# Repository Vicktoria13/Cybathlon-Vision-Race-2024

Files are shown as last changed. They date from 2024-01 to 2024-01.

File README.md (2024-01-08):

# Projet Cybathlon 2024: prise en main des ressources

Le Cybathlon-VIS est une compétition scientifique et technologique, au cours de laquelle des personnes en situation de handicap vont participer à des épreuves, le tout accompagné d’une équipe de scientifiques, démontrant ainsi l’apport des technologies pour les personnes handicapées. En 2024 se tiendra la prochaine édition de la compétition. Pour la première fois, une série d'épreuves est organisée pour des compétiteurs malvoyants/non voyants.  Notre projet est de développer une technologie permettant de répondre aux objectifs de la compétition pour remplir les objectifs de l'épreuve.

[Cybathlon VIS 2024](https://cybathlon.ethz.ch/en/event/disciplines/vis)

Les règles sont spécifiés au lien [Cybathlon rules](https://cybathlon.ethz.ch/documents/races-and-rules/CYBATHLON%202024/CYBATHLON_RacesAndRules_2024.pdf)

Nous nous concentrons sur l'épreuve de la piste jonchée d'obstacles ci-dessous visible.

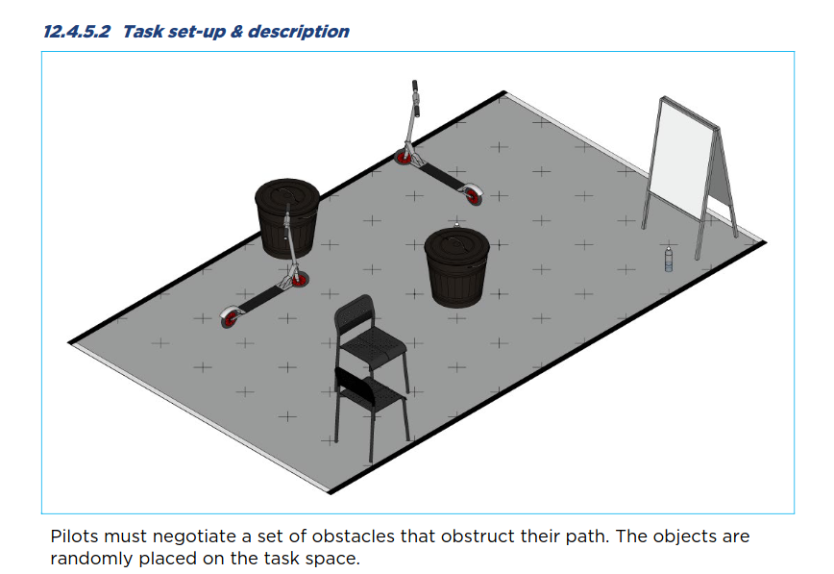
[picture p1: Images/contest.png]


Différents obstacles seront placés sur une piste de 3* 5mètres. Notre projet consiste a développer une architecture mécanique et logicielle capable de guider de manière kinésthésique un pilote non voyant, qui pourra être préalablement entrainé.

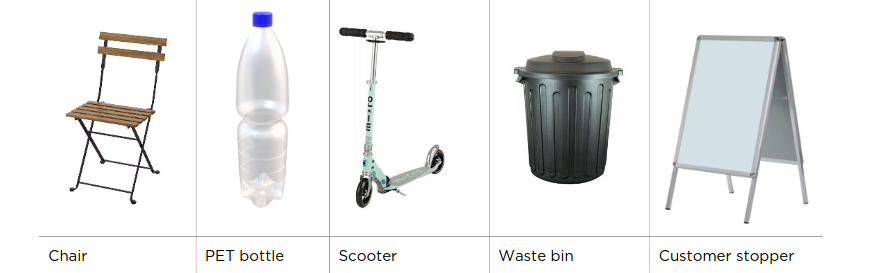
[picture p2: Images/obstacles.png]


Ce projet a été mené en équipe de 4 étudiants, et encadrés par nos professeurs et chercheurs de l'[ISIR](https://www.isir.upmc.fr/) et de [Polytech Sorbonne](https://www.polytech.sorbonne-universite.fr/formations/robotique). Il s'agit d'un projet d'une durée d'un an, durant l'année scolaire 2022/2023.

#  Cahier des charges

Nous avons élaborer un cahier des charges reprenant toutes nos contraintes, et toutes les attentes vis a vis de ce projet. Il est disponible sous format pdf dans le dossier __Documentation__. 
On trouvera également dans ce dossier une explication pdf de nos plans et idées préliminaires, nos schémas, calculs et simulation.

# CAO et simulation

Le git contient un dossier __CAO SolidWorks__ contenant :

* Nos modélisations de toute l'architecture mécanique

* Leurs mises en plan norme ISO

* Une doc technique du matériel et outils utilisés

A ce stade, deux prototypes ont été réalisés au [Fablab de Sorbonne Universite](https://fablab.sorbonne-universite.fr/) ainsi qu'a l'atelier de Polytech.

La documentation, et en particulier le dossier de conception détaillé, reprend de manière précise les étapes de conception.

## Simulation de l'espace de travail du pantographe

Nous avons implémenté le modèle géométrique direct du pantographe, ainsi que son espace de travail, sous Matlab. Il est disponible dans le dossier __Simulation__.
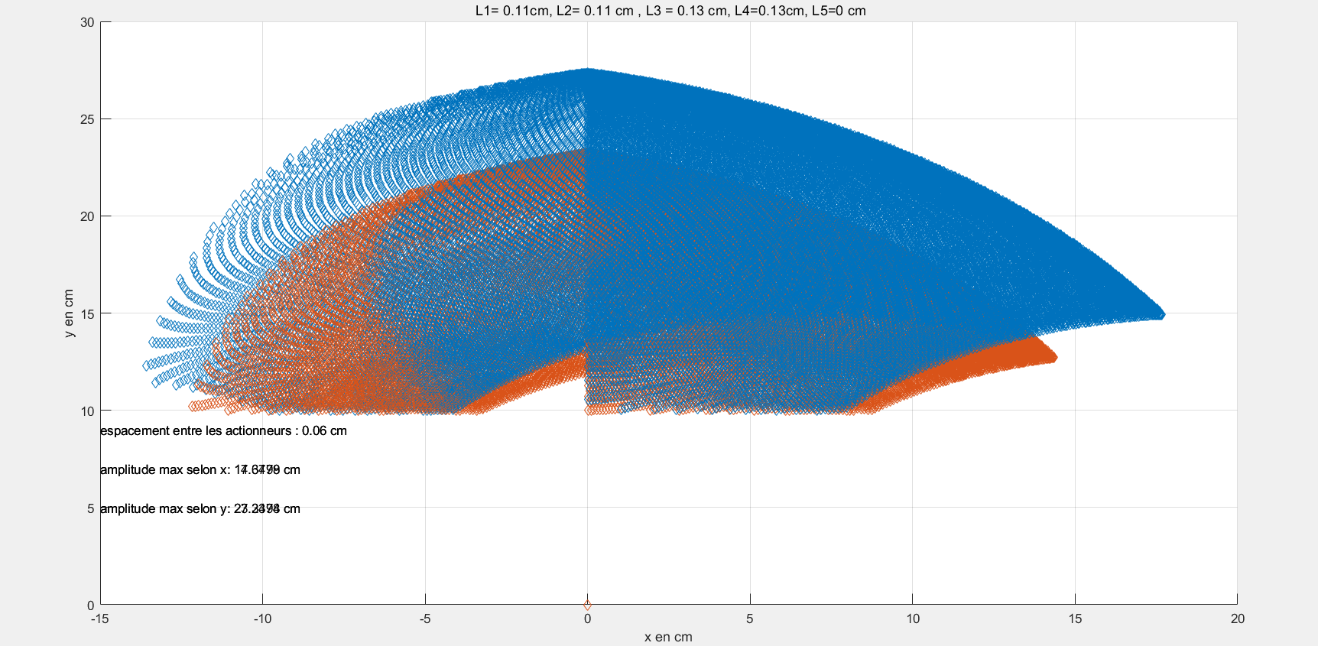
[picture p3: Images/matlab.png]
Simulation WORKSPACE
 

Il permet de visualiser dans un plan 2D l'espace de travail, et dans une 3e dimension, on peut voir le couple demandé sur l'actionneur en question. Quelques points sont abbérants et ont été coupés.

**Remarque**

Le modèle géométrique direct est une approximation du modèle réel. En effet, il ne prend pas en compte les frottements, les jeux mécaniques, les pertes de puissance, etc. Il est donc nécessaire de prendre en compte ces paramètres dans la réalisation du pantographe.

De plus, la force réelle du pilote a été volontairement surévaluée.

Il est possible de changer les paramètres des longueurs des bielles au début du code, et voir les répercussions sur l'espace de travail.

# Architecture logicielle

L'algorithme du projet repose sur une architecture de briques, utilisables sous ROS2 Humble. 

Ce dossier contient plusieurs workspaces ROS2 : 

* Le workspace pour le wrapper de la caméra
* Un workspace pour lancer Octomap / la Naviguation
* Un workspace pour le controle des moteurs.

ZED2

## Installation du wrapper de la caméra

Cette partie vise à décrire les étapes d’installations des paquets et dépendances 
nécessaires à l'utilisation de la caméra sous ROS2.

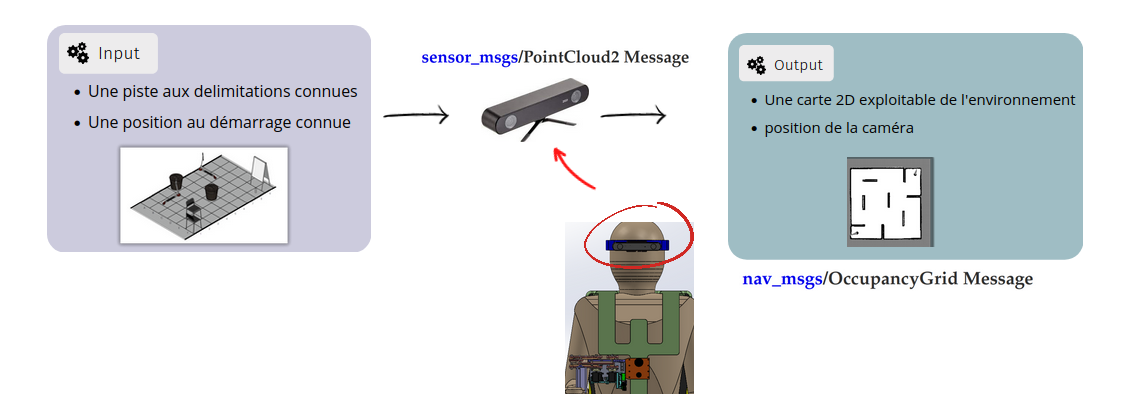
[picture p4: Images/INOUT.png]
INOUT


### Prérequis 

* Ubuntu 22.04
* ROS2 Humble
* Un ordinateur avec une carte graphique NVIDIA

Il est nécessaire d’installer plusieurs dépendances, avant de pouvoir utiliser la caméra via ROS2.

* CUDA : [ version 11.8 et toutes ses dépendances](https://developer.nvidia.com/cuda-downloads)
*ZED SDK v4.0 via [ZED2](https://www.stereolabs.com/developers/release/)

**Remarque** :
1-Attention aux versions d’openCV utilisées. En effet, les dernières versions peuvent ne pas être compatibles avec CUDA. Se renseigner sur le site de CUDA.

2- L’installation peut prendre un certain temps

### Utilisation sous ROS2

Dans le cadre de ce projet, nous utilisons ROS2 afin de pouvoir communiquer le résultat de l’algorithme de mapping, le SLAM, via des topics ROS2, et de pouvoir en exploiter le résultat.

Le SDK de la caméra fournit un fichier lançant le noeud de la caméra , et permettant de démarrer tous les topics disponibles.

Une fois le wrapper installé dans le fichier source, et le paquet compilé via

```$ colcon build --symlink-install --cmake-args=-DCMAKE_BUILD_TYPE=Release   ```

Exécuter la commande :

```$ ros2 launch zed_wrapper zed.launch.py ```

Cette première commande lance tous les noeuds et topic liés a la caméra, notamment le topic d'odométrie et du nuage de points via la SLAM.

### Paramètres
Dans le SDK de la ZED2 se trouve un fichier, commun a tous types de ZED, avec des paramètres internes. Voici son chemin :

``zed-ros2-wrapper/zed wrapper/config/common.yaml ``

Dans ce fichier, on peut regler plusieurs paramètres qui peuvent nous interesser.

* mapping_enabled doit être mis a True pour permettre le SLAM

* initial_base pose permet de definir la position de démarrage de la caméra : par défaut, a l'allumage, la caméra est a (0,0,0).

* depth_min_range : il s'agit de la distance minimale a laquelle la camera essayera de detecter un objet. Cela peut etre utile si on ne veux pas que le bout du pantographe soit compté comme un obstacle ! Par défaut , même si on la met a 0, la caméra ne peut techniquement pas detecter a moins de 30 centimètres.

### Tests et Comparaison : choix des modes

La ZED2 possède 4 modes. Nous choisissons le mode NEURAL #4.

Attention : 

* Il est nécessaire de l'entrainer une première fois au démarrage

* Il s'agit du mode le plus gourmand : voir [Depth modes](https://www.stereolabs.com/docs/depth-sensing/depth-settings/). Il peut doncêtre utile dans les paramètres du wrapper de spécifier une plus grande taille mémoire en % alloué.

Ce mode nous est pertinent car du au réseau neuronal employé, il est bien plus performant pour reconstituer des objets/obstacles.
La qualité du point cloud est sensiblement meilleure que les 3 autres, avec plus de points, donc plus de précisions.

![image_graph](Images/neurone.png)

**Remarque**

La bouteille fait partie des obstacles a éviter lors de l'épreuve. On suppose qu'elle est transparente et contient de l'eau. Selon les conditions d'éclairement , elle peut ainsi être difficilement perçue.

## Installation de OCTOMAP

Suivre le tutoriel : [Octomap](https://github.com/OctoMap/octomap)  
Il s'agit d'une librairie qui prend en entrée message ROS2 ``sensor_msgs/PointCloud2 Message``, filtre le nuage de points, et le projette sur un plan 2D , donnant une occupancy grid.

![octree](https://encrypted-tbn0.gstatic.com/images?q=tbn:ANd9GcReFk687xEfCUiTUhuMOMQlDOeW7LCxsLnciQ&usqp=CAU)

Pour lancer le noeud ``octomap_server`` :

 ``ros2 launch octomap_server octomap_mapping.launch.xml``

Les topics interessants :

* octomap_point_cloud_centers : centre de chaque voxel.
* map : resultat de la projection sur un plan 2D. Le résultat est de type ``nav_msgs/OccupancyGrid``. autre nom : projected_map.

#### fichier xml de lancement

Il est nécessaire dans le fichier xml, situé dans ``octomap_mapping/octomap_server/octomap_mapping.launch.xml`` de spécifier le nom du topic ou se situe le nuage de points (message ROS2). Ainsi, il faudra changer s'il faut la ligne

``<remap from="cloud_in" to="/zed2/zed_node/mapping/fused_cloud"/>``

Ces 2 lignes servent a cropper en Z (verticale vers le haut) le nuage de point d'octomap. Il peut être changé en fonction de la luminosité et du volume des obstacles traités :

``<param name="occupancy_min_z" value="0.2"/> ``
``<param name="occupancy_max_z" value="1.8"/>``

Enfin , ``<param name="filter_speckles" value="true"/>`` sert a préfiltrer l'octree, en elevant les points isolés.

![image_graph](Images/octomapGraph.png)

### Sauvegarde de l'occupancy grid (2D)

dans le fichier ``map_result_Cybathlon`` se trouve une sauvegarde de l'occupancy grid et de l'octree. On peut sauvegarder en executant les commandes :

``ros2 run nav2_map_server map_saver_cli -f path``

 et 

 `` ros2 run octomap_server octomap_saver_node --ros-args -p octomap_path:=my_house.ot``

 ![image_graph](Images/graph.png )

 ## Resultat et observation sous Rviz2

  ![image_graph](Images/occupancy.png)

Au commencement, on suppose que le pilote est au milieu de la piste, orienté face a la ligne d'arrivée. Les zones inconnues , non vues par la caméra, sont supposées libre (pixel a 0).
Des délimations manuelles sont mises, afin de délimiter l'espace de l'occupancy grid : on rappelle qu'il s'agit d'une piste de 3*5m.

![image_graph](Images/start.png)

**Important**

Il est possible manuellement dans les paramètres de la zed de spécifier que l'on démarre a une hauteur z du sol. Notre caméra etant placé sur la tête du pilote, il nous aurait fallu spécifier la taille du pilote. Cependant , pour des raisons inconnues, en spécifiant une valeur, on constate lors des essais, que le nuage de point a tendance a se pencher. Pour cela, nous avons fait le choix de démarrer a 0, ce qui nous évite temporairement ce problème. Il faut donc absolument que le pilote démarre avec la caméra posée a terre, et au milieu de la piste.

### Navigation

L'objectif de la navigation est d'obtenir une direction que le pilote devra suivre afin d'arriver à la position souhaitée. Nous recevons en entrée une occupancyGrid de Octomap correspondant à un tableau une dimension avec la probabilité que chaque pixel contienne un obstacle. Si l'obstacle est confirmé la valeur 100 est assignée à ce pixel, si on sait que la zone est vide nous aurons une valeur de 0 et si le pixel n'est pas encore déterminé une valeur de -1 est définie.

Connaissant la position des obstacles il ne reste plus qu'à obtenir un chemin pour parcourir le graphe et atteindre l'arrivée. Ceci est réalisé grâce à un algorithme de navigation nous renvoyant une direction optimal à suivre que nous pouvons envoyer aux moteurs afin de guider le pilote.

![A* Animation](Images/Astar_progress_animation.gif) 

## Algorithme Dijkstra : 
**Fonctionnement :** 

On délimite un rayon autour de la position initiale et nous parcourons tous les points du cercle. Tant que le point d'arrivée n'est pas atteint, le rayon de notre cercle augmente pour rechercher des intersections de plus en plus loin de notre point de départ.

**Incovéviant :**

Si on connait la position de notre point d'arrivée nous perdons un temps assez important afin de trouver un chemin optimal.
C'est pour cela que nous utilisons l'Algorithme A*.

## Algorithme A*

**Fonctionnement :**

A* est une extension de l'algorithme Dijkstra plus performante et optimal pour trouver un chemin, en effet connaissant la position de départ et la position finale, le chemin le plus court pour atteindre la destination est la ligne droite.
L'algorithme va donc parcourir le graphe en se dirigeant directement vers la position à atteindre.

![A* Schéma Fonctionnel](Images/a_star_schema_fonctionnel.png) 

**Avantages :**

* Consomme très peu de mémoire
* Plus rapide pour calculer un chemin que l'Algorithme Dijkstra.

**Inconvénients :**

* Si la position a atteindre est sur un obstacle il est impossible de trouver un chemin afin d'atteindre la position souhaitée
* Si le chemin optimal pour atteindre la position finale n'est pas dirigé vers la position finale mais à l'opposé il sera un peu plus long pour calculer la trajectoire. Cependant, comme nous savons par avance qu'au maximum 10 obstacles seront présents sur la piste, nous supposons que ce cas se présentera rarement et que nous privilégions un temps de parcours plus court pour les cas les plus fréquents.

![A* Incovénient](Images/a_star_probleme.png) 

# Utilisation sous ROS2
Afin de lancer cet algorithme sous ROS2 nous utilisons la ligne de commande : 

```ros2 run navigation_py dijkstra_node```

De plus, nous pouvons utiliser l'algorithme de traduction de l'information grâce à la commande :

```ros2 run navigation_py direction_node_ss_bool```
	
Cet algorithme prend en entrée l'angle obtenu par l'algorithme a* et envoie une position à atteindre aux moteurs pour guider le pilote dans la direction souhaitée. L'information sera ensuite reçu par une nouvelle node que l'on peut lancer avec :

```ros2 run pyxbox commande_moteur```

### microROS

MicroROS est un moyen de communication entre un microcontrolleur et ROS2. Nous l'utilisons pour transmettre certaines informations au pilote telle que la position d'origine. Cela peut lui permettre d'avoir un point de repère fixe, pour cela nous implémentons un vibreur sur la poignée du pantographe qui s'activera lorsque la poignée est à la position d'origine.

**Installation :**

L'installation de microROS peut être compliqué lorsque Nav2 est déjà installé sur l'ordinateur. 
3 lignes de commandes sont nécessaires afin de faire l'installation :

```git clone -b $ROS_DISTRO https://github.com/micro-ROS/micro_ros_setp.git src/micro_ros_setup```

```sudo apt update && rosdep update```

```rosdep install --from-path src --ignore-src -y```

**Prérequis :**

* Microcontrolleur ESP32.

**Avantages :**

Si le pilote perd l'information sur la direction, il sera en mesure de la retrouver par un passage à l'origine.

**Inconvénients :**

Nous avons pu remarquer un léger retard lorsque le vibreur s'active pour la position d'origine.
De plus, nous avons pu remarquer que nous ne pouvons pas travailler avec des informations analogiques avec microROS, seulement le numérique est supporté pour le moment. 

**Utilisation :**

6 commandes sont nécessaires afin de pouvoir lancer le code microROS, ces 6 commandes se lancent depuis le même terminal :

```ros2 run micro_ros_setup configure_firmware.sh microROS_sub --transport serial```

```ros2 run micro_ros_setup build_firmware.sh```

```ros2 run micro_ros_setup flash_firmware.sh```

```ros2 run micro_ros_setup create_agent_ws.sh```

```ros2 run micro_ros_setup build_agent.sh```

```ros2 run micro_ros_agent micro_ros_agent serial --dev /dev/ttyUSB```

Ce code n'est pas encore implémenté dans le code final du projet, cependant il est tout à fait possible de tester son fonctionnement en lui envoyant une information directement depuis un second terminal afin d'activer le vibreur :

```ros2 topic pub --once/micrROS std_msgs/msg/Int32 '{data: 1}'```

## Prise en main du package controle des moteurs

* Les moteurs sont des Dynamixel MX-28R (Protocol 2.0)

![Moteur](Images/moteur.jpg)

## Installation de la SDK de Dynamixel

Cette partie vise à décrire les étapes d’installations des paquets 
nécessaires à l'utilisation des moteurs sous ROS2.

### Prérequis 

* Ubuntu 22.04
* ROS2 Humble

### Installation

Vous n'avez pas d'installation a effectué, juste à mettre notre package dans le src : DynamixelSDK (Moteur) et pyxbox (Contrôle via la manette/Algorithme)

Si vous faites une installation sans prendre nos packages
* Dynamixel SDK : [Installer via le site](https://emanual.robotis.com/docs/en/software/dynamixel/dynamixel_sdk/download/#repository)
Package à installer dans le src du workspace de ROS2

Installation de l'interface
* Dynamixel Wizard 2.0 : [Installer via le site](https://emanual.robotis.com/docs/en/software/dynamixel/dynamixel_wizard2/)
Aller à la partie "Software Installation" et suivre les étapes.

### Utilisation de Wizard

* Pour pouvoir voir ses moteurs dans l'interface, il faut tout d'abord scannez ces derniers. Dans l'onglet "Options" : vous pouvez choisir un Scan des ID de 0 à 2 pour faciliter la rapidité d'exécution (Nous avons mis manuellement les ID 1 et 2). Ne pas oublier de sélectionner le port pour les moteurs (Select All pour plus de simplicité).
* Vous pouvez allumer la Led d'une des moteurs pour savoir quel moteur correspond à quel ID. Le torque permet d'allumer l'asservissement des moteurs.
* Si vous recherchez plus d'informations pour l'interface, vous pouvez checker le site de Dynamixel Wizard. Vous pouvez aussi checkez ce site : [Site spécifique des moteurs](https://emanual.robotis.com/docs/en/dxl/mx/mx-28-2/)

### Utilisation sous ROS2

Dans le cadre de ce projet, nous utilisons ROS2 afin de pouvoir controler les moteurs.

Nous avons un paquet permettant le mode manuel, c'est-à-dire le contrôle extérieur depuis une manette de jeu xBOX. Les commandes ci-dessous précisent comment lancer les noeuds.

Une fois la mise en place des packages dans le src, il faut compiler via la commande :

``` $ colcon build ```

* Pour lancer les moteurs :

Avant de lancer les moteurs, n'oubliez pas de mettre le bouton ON sur la carte de commande 

```$ ros2 run dynamixel_sdk_examples d_node ```

Il se peut que le code vous renvoie une erreur :
* Soit vous avez oublié de disconnect les moteurs sur Wizard
* Soit il faut changer le port USB dans le code d_node.cpp

C'est à la ligne 54 qui se trouve dans le path "src/DynamixelSDK/dynamixel_sdk_examples/src/d_node.cpp

* Pour lancer la manette :

![PhotoManette](Images/Manette_xbox.jpg)

        Brancher l'adaptateur au PC
        Appuyez sur le bouton de l'adaptateur jusqu'a ce qu'il clignote
        Appuyez sur le bouton central de la manette Xbox
        Appuyez sur le bouton à côté de la touche "LB" jusqu'à ce que l'adaptateur arrête de clignoter

Effectuez ces 2 commandes pour que le PC soit connecté à la manette : 

```$ sudo chmod -R 777 /dev/bus/usb/ ```
``` $ xboxdrv --no-uinput --detach-kernel-driver ```

Vous pouvez faire CTRL+C une fois que c'est bon

Avant toute chose, il faut être sur que la manette est bien connectée, pour cela, vous pouvez lancer un script python qui se trouve dans le path "src/pyxbox/pyxbox/sample.py"
Il faut que Connected affiche un Y et non N !

``` python3 sample.py ```

Il faut bouger le joystick et les valeurs changent.

![PhotoManette](Images/manette.png)

Ligne de code pour lancer la node de la manette :

```$ ros2 run pyxbox manette_moteur ```

Il se peut que la manette ne fait pas bouger le robot :
* Soit la manette n'est pas connectée
* Soit les moteurs ont des valeurs aberrantes au lancement, il faut alors relancer les moteurs en appuyant sur OFF sur la carte de commande et refaire la manipulation de ces derniers.

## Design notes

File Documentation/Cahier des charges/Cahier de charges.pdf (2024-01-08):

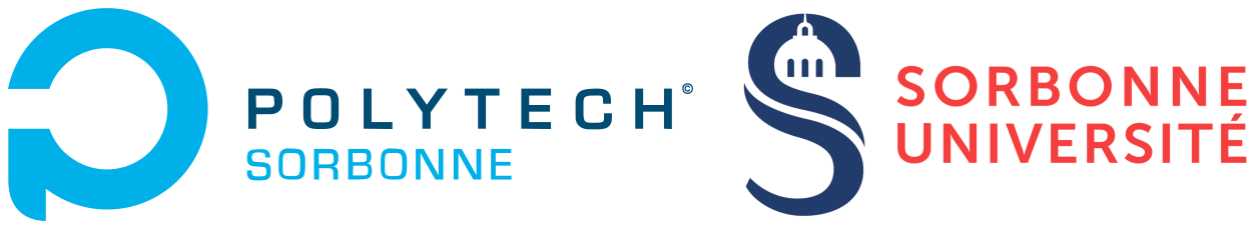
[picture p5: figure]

# Guidage kinesthésique pour l'assistance aux malvoyants

# Cahier des charges

### Projet Industriel d’année 4 Spécialité Robotique

NGUYEN Victoria

FU Daniel

SHLYKOVA Olga

MOREL Théo

Encadrant : Lilian CARILLET

Client : Fabien VERITE

Pilote : Sébastien HINDERER

# Sommaire

Introduction | 3
Analyse du besoin | 3
Analyse fonctionnelle du besoin | 4
Moyen | 7
Calendrier | 7
Conclusion | 7
Annexe | 7
ROB4 | Projet Industriel

Introduction

Le Cybathlon-VIS est une compétition scientifique et technologique, au cours de laquelle des personnes en situation de handicap vont participer à des épreuves, le tout accompagné d’une équipe de scientifiques, démontrant ainsi l’apport des technologies pour les personnes handicapées. En 2024 se tiendra la prochaine édition de la compétition. Pour la première fois, une série d'épreuves est organisée pour des compétiteurs malvoyants/non voyants. Notre projet est de développer une technologie permettant de répondre aux objectifs de la compétition pour remplir les objectifs de l'épreuve.

Analyse du besoin

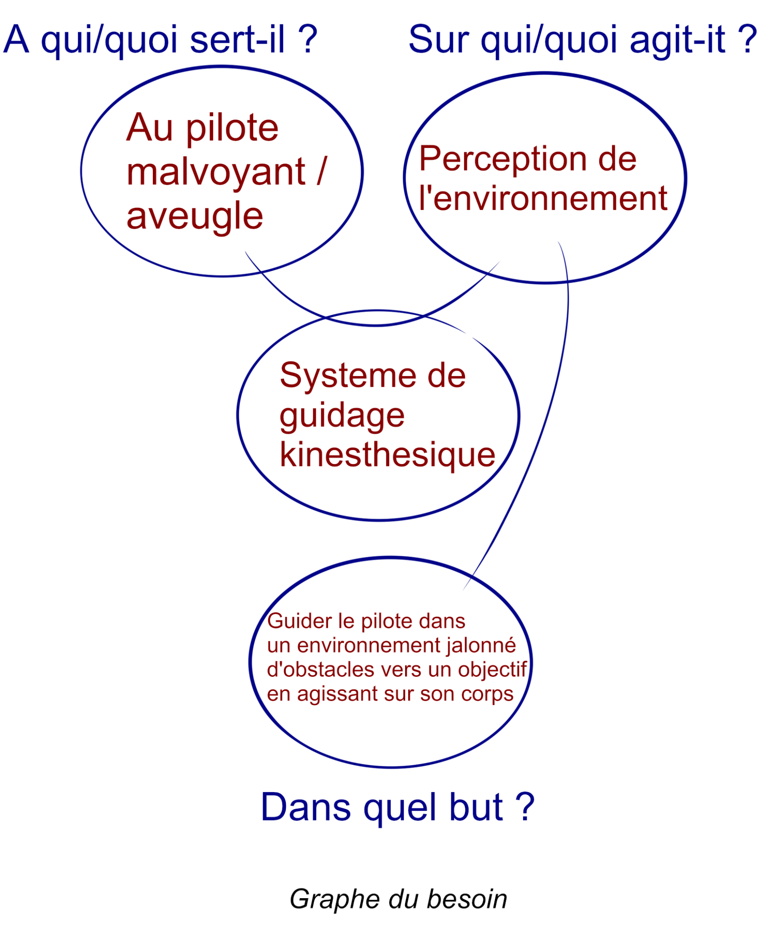
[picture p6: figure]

Enoncé du besoin : Le produit sert au pilote (Sébastien Hinderer) mal/non voyant en agissant sur sa perception de l'environnement, dans l'objectif de le guider dans un environnement jalonné d'obstacles dans le cadre de la compétition.

ROB4 | Projet Industriel

Contrôle de validité :

Nous avons besoin de ce système parce que :

Il est difficile pour les malvoyants de naviguer dans leur environnement sans assistance; Il n’existe pas sur le marché de système à retour positif pour guider les malvoyants - le système SGK permet d’éviter un obstacle de l’environnement qui ne serait pas possible avec un chien ou une canne, notamment vis à vis de la hauteur des obstacles
Le guidage actuel employé le plus répandu est par mouvement initié par les guides d’aveugles - le retour kinesthésique employé par le système est le moyen le plus familier et donc le plus pertinent dans ce projet.

Nous avons besoin de ce système pour :

Guider les malvoyants dans l'environnement du cybathlon;
Donner une autonomie aux malvoyants pendant les compétitions du cybathlon;

Disparition du besoin :

Le besoin n’existerait plus si un moyen médical était trouvé pour soigner la cécité et la malvoyance; Un autre moyen est développé pour donner l’autonomie aux malvoyants;
Le besoin n’existerait plus si la compétition devait être annulée.

Analyse fonctionnelle du besoin

SGK : Système de Guidage Kinesthésique

Les phases de vie du produit :

Phases | Sous-phases | Qui est concerné | Contraintes/critères | U / HU*
Système seul | Conception | Equipe projet industriel | | HU
| Fabrication | Fournisseurs
| Montage | Equipe projet industriel
Système porté par le pilote | Arrêt | Pilote | Environnement Securite/confort du pilote | U
| Fonctionnement | Pilote | Environnement Securite/confort du pilote Ergonomie | U
| Maintenance | Pilote et equipe Cybathlon | Niveau de la panne | U et HU
Fin de vie | Démontage | | | HU
| Recyclage
*U - En utilisation | HU - Hors utilisation
ROB4 | Projet Industriel

Fonctions :

FP1: Guider le bras du pilote pour l’amener vers un objectif

Contraintes :

FC1 : S’adapter au pilote
FC2 : Atteindre un objectif
FC3 : Éviter les obstacles
FC4 : S’adapter au bras
FC5 : S’adapter au milieu ambiant

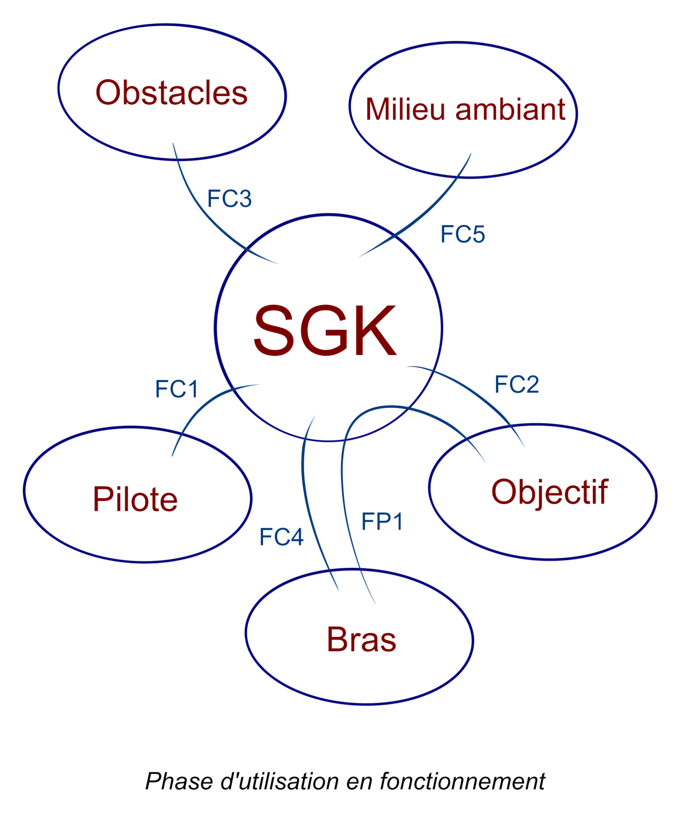
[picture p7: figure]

Tableau de caractérisation des fonctions et des contraintes en fonctionnement:

Fonctions | E.M.U* | Critères | Niveaux | Flexibilité
FP1: Guider le bras du pilote pour l’amener vers un objectif | | | | Guider c’est : - Exercer une action sur le bras du pilote l'amenant dans une direction déterminée | - Trouver un chemin à travers la piste de l'épreuve Cybathlon grâce à la technologie ROS - Guider le pilote suivant ce chemin - Exercer une force souple/douce | 2 0 0
FC1 : S’adapter au pilote | | | | S’adapter c’est : - Sécuriser le pilote à chaque instant - Être conforme à la physionomie humaine - Être conforme aux dimensions du pilote attitré | - Tension et courant utilisés - Poids : <10kg - Taille et morphologie du pilote - Espace de travail 50 x 50 cm | 0 3 3
FC2 : Atteindre un objectif | | | | Atteindre c’est : - Permettre à la personne malvoyante de se déplacer librement comme tout autre personne | - Connaître le trajet optimal dans une pièce | 1

Bras :
Caractéristiques
dimensionnelles
du pilote
(Sébastien
Hinderer)

Objectif :
Réalisation de
l’épreuve du
Cybathlon
(Annexe 1)

Pilote :
Caractéristiques
définies par le
pilote attitré du
client

Objectif :

ROB4 | Projet Industriel

FC3 : Éviter les obstacles | Eviter c’est : - S’assurer de la sécurité de la personne vis à vis des obstacles - Enlever la collision avec des obstacles. | - Détecter chaque obstacle (droite-gauche & devant-derrière) afin de ne pas mettre en danger la personne. - Détecter chaque obstacle (haut-bas) | 1 3
FC4 : S’adapter au bras | S’adapter c’est : - Transmettre l’information du système au bras du pilote - S’assurer d’une rigidité/flexibilité suffisante | - Transmettre l’information par moyen kinesthésique - Importance d’une structure rigide et flexible | 2 1
FC5 : S’adapter au milieu ambiant | S’adapter c’est : - avoir un système fonctionnel et éviter les dysfonctionnements fréquents | - Importance négligeable étant donné un environnement normal | 3

Obstacles :
Conditions
définies par le
Cybathlon

Bras

Milieu Ambiant :
Conditions
intérieures
définies par le
Cybathlon
(Annexe 2)

*E.M.U - Élément du milieu d’utilisation

Contraintes :

FC1 : Ne pas contraindre le pilote FC2 : Résister aux obstacles
FC3 : S’adapter au milieu ambiant

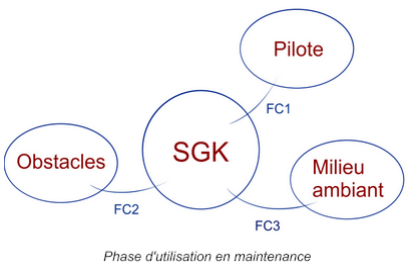
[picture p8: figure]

Tableau de caractérisation des fonctions et des contraintes en maintenance :

Fonctions | E.M.U* | Critères | Niveaux | Flexibilité
FC1 : S’adapter au pilote | | S’adapter c’est : - Résister aux mouvements du pilote - Ne pas nuire à la sécurité du pilote. - Ne pas le blesser - Maintenance possible par le pilote en cas de besoin | - Courant utilisé | 0
FC2 : S’adapter aux obstacles | | | | S’adapter c’est : - Avoir un système robuste permettant d’éviter un dysfonctionnement hors fonctionnement. | - Rigidité matériaux | 1

Pilote :

Obstacles :

ROB4 | Projet Industriel

FC3 : S’adapter
au milieu
ambiant

Milieu
Ambiant :

S’adapter c’est :
- Avoir un système fonctionnel et éviter les
dysfonctionnements
fréquents
- Avoir un système où il est facile d’intervenir en cas de problèmes techniques.
- Importance
négligeable étant
donné un
environnement
normal

3

*E.M.U - Élément du milieu d’utilisation

Moyen

- 1 salle de projet disponible tous les vendredis.
- 1 encadrant de projet (Lilian Carillet)
- 1 ingénieur roboticien (Aline Baudry) + 1 ingénieur électronicien (Sylvain Viateur) en support technique/expertise.
- Matériels : Caméra Kinect + harnais

Le budget alloué pour ce projet par le client est de 1000 euros (+300 euros de Polytech).

Calendrier

Phase 1 : Cahier des charges (23 octobre 2022)

Phase 2 : Conception préliminaire (11 décembre 2022)

Phase 3 : Conception détaillée (12 février 2023)

Phase 4 : Réalisation (Indéterminé !)

Phase 5 : Tests (Indéterminé !)

Conclusion

La technologie voulue répond à un besoin en agissant de manière précise sur son utilisateur. Chaque fonction impliquant le système et/ou les éléments extérieurs ont été identifiées, et permettent de dégager clairement notre objectif. La technologie se veut être part de briques technologiques voulues par le client, afin d’être reprise à des fins d’optimisation et d’amélioration. Ainsi, le projet se veut modulable.

ROB4 | Projet Industriel

Annexe

Annexe 1 : | Deroulement des epreuves Cybathlon-VIS (page 159)
Annexe 2 : | Reglement des epreuves (page 14)

https://cybathlon.ethz.ch/documents/races-and-rules/CYBATHLON%202024/CYBATHLON_RacesAndRules_2024_final.pdf (https://cybathlon.ethz.ch/documents/races-and-rules/CYBATHLON%202024/CYBATHLON_RacesAndRules_2024_final.pdf)

Annexe 3 : | Planning Gantt
ROB4 | Projet Industriel

Gantt - Projet “Assistance kinesthésique aux malvoyants”

Semaine numero | 1 | 2 | 3 | 4 | 5 | 6 | 7 | 8 | 9 | 10 | 11 | 12 | 13 | 14 | 15 | 16 | 17 | 18 | 19 | 20 | 21 | 22 | 23 | 24 | 25 | 26 | 27 | 28 | 29 | 30 | 31 | 32

Réaliser le cahier de charges

Identifier le besoin

Valider par le client et apporter les modifications éventuelles

Conception préliminaire

Premières propositions des solutions

Expérimentation avec les solutions

Rédaction de la conception préliminaire

Validation par le client et modifications éventuelles

Conception détaillée

Prise des mesures

Modélisation

Dimensionnement et choix des composants

Algorithme préliminaire

Production

Commande de composants

Production des composants

Assemblage

Electronique et programmation

Validation

ROB4 | Projet Industriel | Page 9/9

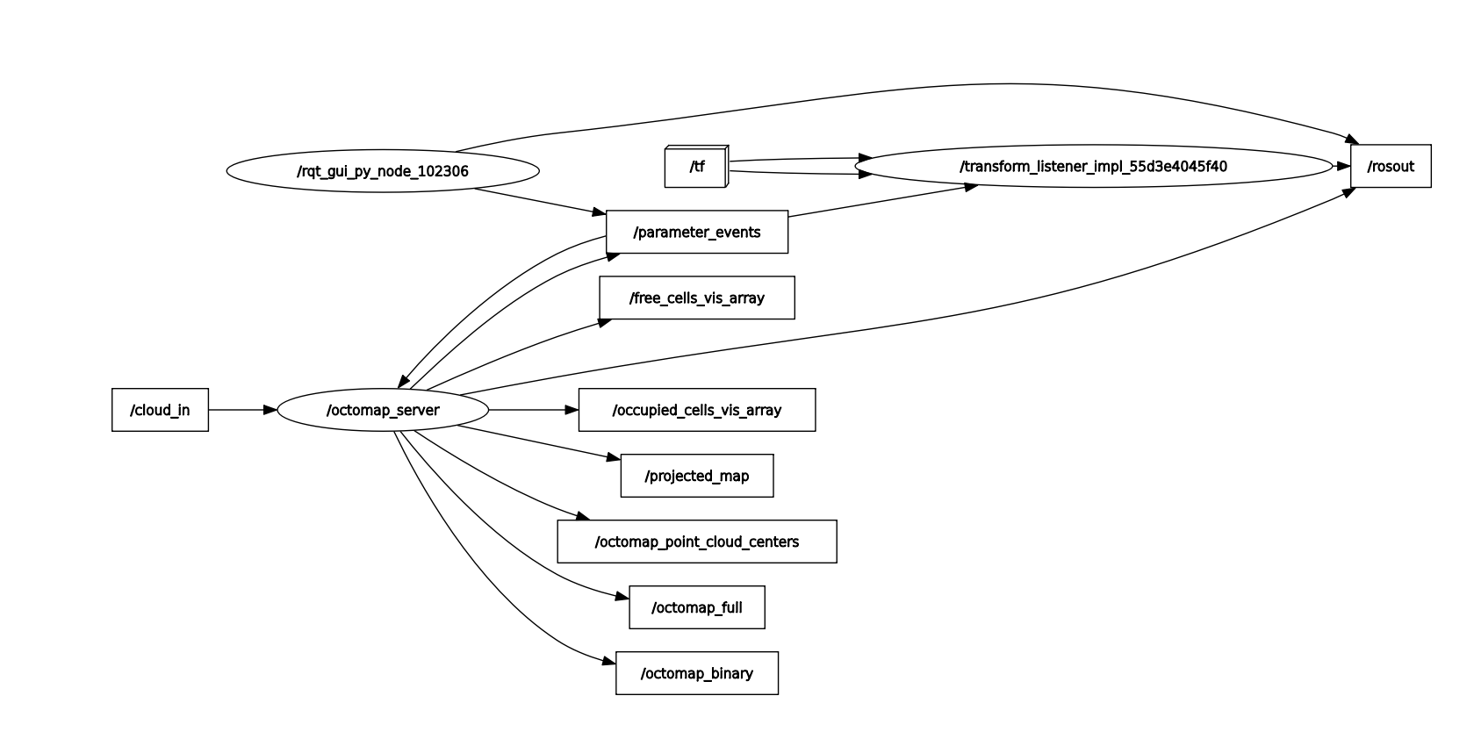
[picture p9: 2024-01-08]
Images/octomapGraph.png

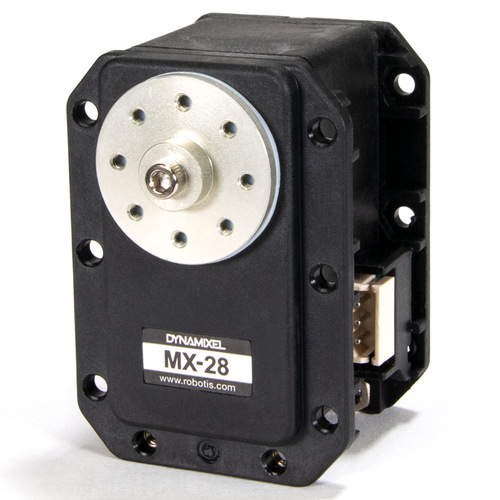
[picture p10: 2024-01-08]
Images/moteur.jpg

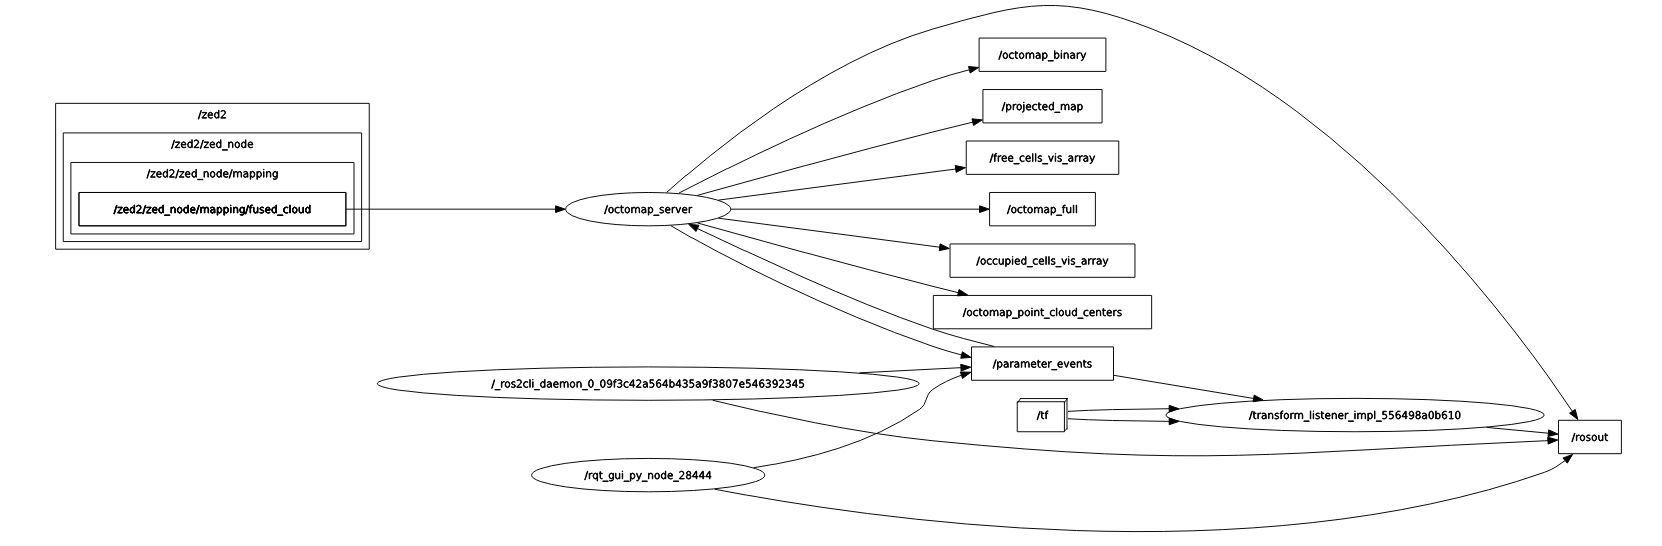
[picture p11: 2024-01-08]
Images/graph.png

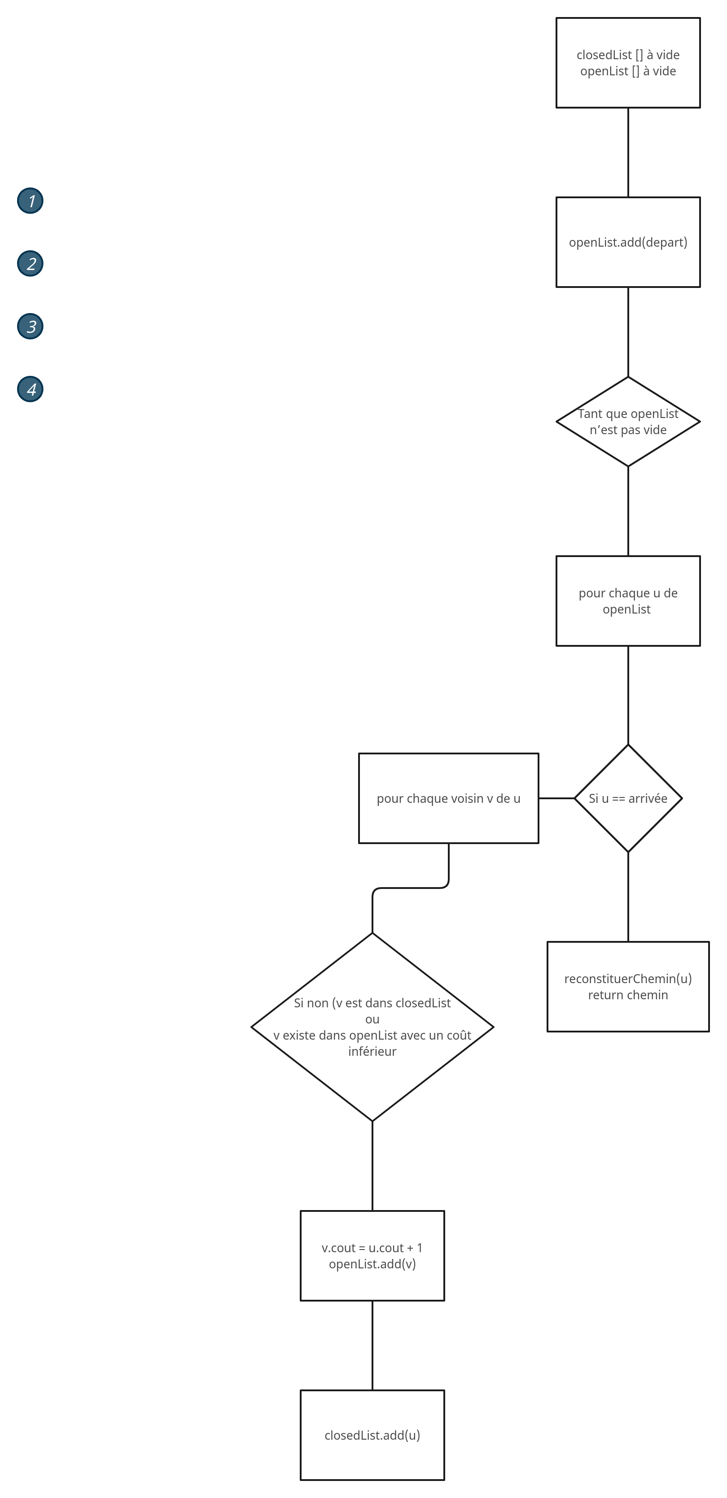
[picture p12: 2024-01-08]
Images/a_star_schema_fonctionnel.png

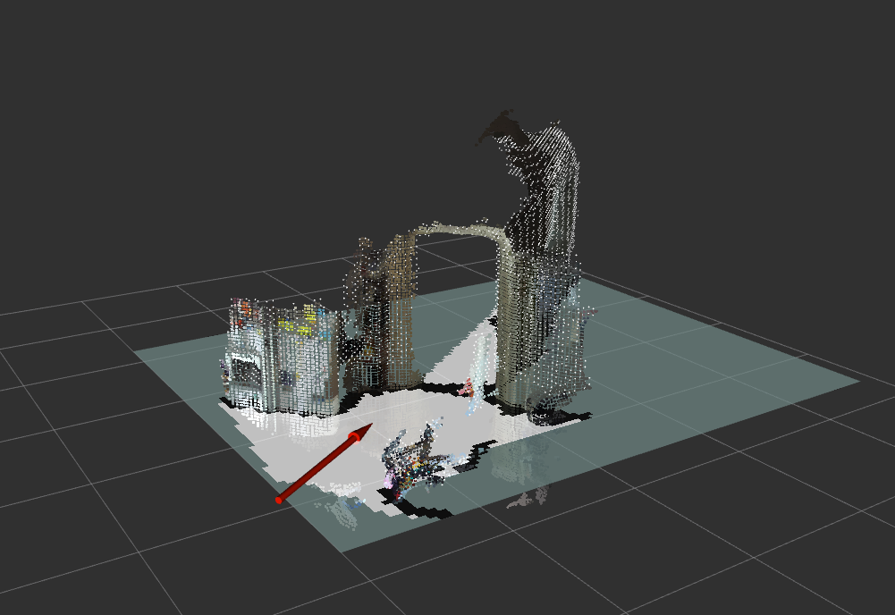
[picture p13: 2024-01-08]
Images/occupancy.png

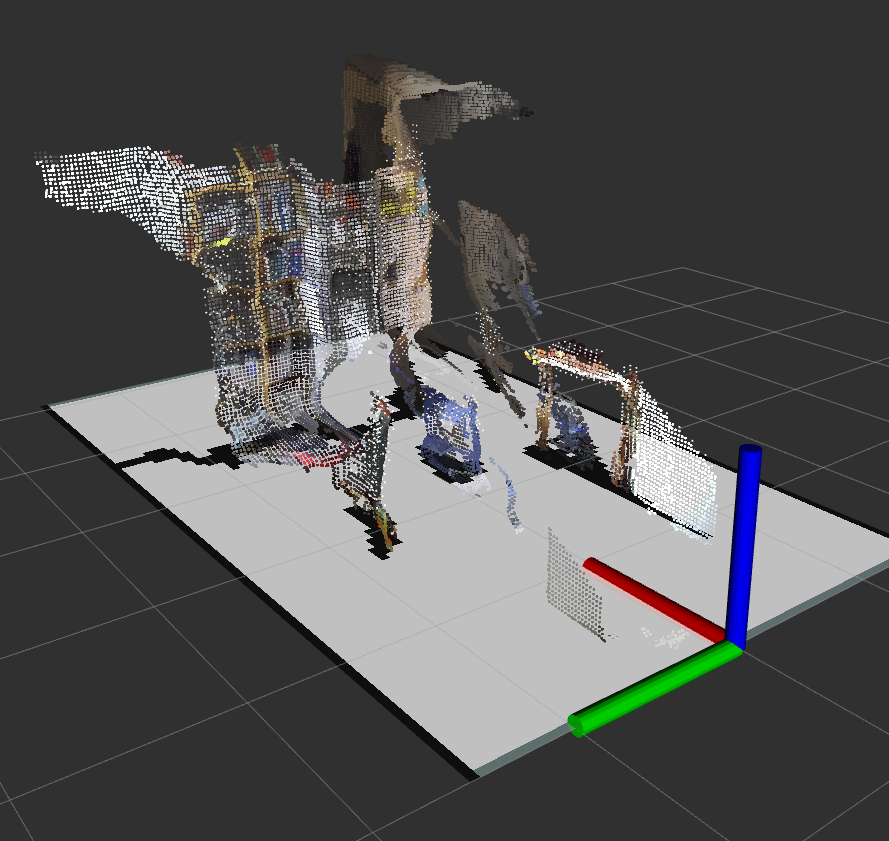
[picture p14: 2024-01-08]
Images/start.png

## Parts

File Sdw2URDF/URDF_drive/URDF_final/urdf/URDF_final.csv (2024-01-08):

Link Name | Center of Mass X | Center of Mass Y | Center of Mass Z | Center of Mass Roll | Center of Mass Pitch | Center of Mass Yaw | Mass | Moment Ixx | Moment Ixy | Moment Ixz | Moment Iyy | Moment Iyz | Moment Izz | Visual X | Visual Y | Visual Z | Visual Roll | Visual Pitch | Visual Yaw | Mesh Filename | Color Red | Color Green | Color Blue | Color Alpha | Collision X | Collision Y | Collision Z | Collision Roll | Collision Pitch | Collision Yaw | Collision Mesh Filename | Material Name | SW Components | Coordinate System | Axis Name | Joint Name | Joint Type | Joint Origin X | Joint Origin Y | Joint Origin Z | Joint Origin Roll | Joint Origin Pitch | Joint Origin Yaw | Parent | Joint Axis X | Joint Axis Y | Joint Axis Z | Limit Effort | Limit Velocity | Limit Lower | Limit Upper | Calibration rising | Calibration falling | Dynamics Damping | Dynamics Friction | Safety Soft Upper | Safety Soft Lower | Safety K Position | Safety K Velocity
Link_1 | -0,0199413257892108 | -0,0326881010817097 | -0,0539823305241484 | 0 | 0 | 0 | 0,389835137136689 | 0,00015774241882171 | -4,33075851251135E-05 | 6,02665925651826E-06 | 0,000512996561655938 | -2,72377701348866E-06 | 0,000492177811827383 | 0 | 0 | 0 | 0 | 0 | 0 | package://URDF_final/meshes/Link_1.STL | 0,752941176470588 | 0,752941176470588 | 0,752941176470588 | 1 | 0 | 0 | 0 | 0 | 0 | 0 | package://URDF_final/meshes/Link_1.STL |  | LINK_1-1 | Origin_global |  |  |  | 0 | 0 | 0 | 0 | 0 | 0 |  | 0 | 0 | 0
Link_2 | 0,0495702828045499 | -1,71622438482899E-12 | -0,0211645200627954 | 0 | 0 | 0 | 0,0655866352340545 | 6,38196817028964E-06 | 1,01564332573474E-15 | 1,29724738063705E-16 | 0,000113847113994669 | -8,70169042332567E-17 | 0,000116612059752427 | 0 | 0 | 0 | 0 | 0 | 0 | package://URDF_final/meshes/Link_2.STL | 0,752941176470588 | 0,752941176470588 | 0,752941176470588 | 1 | 0 | 0 | 0 | 0 | 0 | 0 | package://URDF_final/meshes/Link_2.STL |  | LINK2-2 | Origin_Joint_1_2 | Axis_Joint_1_2 | Joint_1_2 | continuous | 0,029949 | 0,0017526 | 0 | 0 | 0 | 0,53734 | Link_1 | 0 | 0 | -1
Link_3 | 0,0681323965481278 | 2,99760216648792E-15 | -0,0232121045572643 | 0 | 0 | 0 | 0,020871872248541 | 1,03086571713126E-06 | 2,52521697400188E-20 | -1,2081360240033E-20 | 2,75270107115966E-05 | 7,70719318768475E-22 | 2,84221546645072E-05 | 0 | 0 | 0 | 0 | 0 | 0 | package://URDF_final/meshes/Link_3.STL | 0,752941176470588 | 0,752941176470588 | 0,752941176470588 | 1 | 0 | 0 | 0 | 0 | 0 | 0 | package://URDF_final/meshes/Link_3.STL |  | LINK3-1 | Origin_Joint_2_3 | Axis_Joint_2_3 | Joint_2_3 | continuous | 0,13 | 0 | 0 | 0 | 0 | 2,0078 | Link_2 | 0 | 0 | -1
Link_4 | -0,0246615167632169 | -0,000499829688404133 | 0,0276355679134506 | 0 | 0 | 0 | 0,0660845351410077 | 4,10506606098931E-05 | 1,34672878617248E-07 | -5,68057512578542E-09 | 6,47760548114758E-05 | 9,57998852789668E-10 | 3,21605531286784E-05 | 0 | 0 | 0 | 0 | 0 | 0 | package://URDF_final/meshes/Link_4.STL | 0,752941176470588 | 0,752941176470588 | 0,752941176470588 | 1 | 0 | 0 | 0 | 0 | 0 | 0 | package://URDF_final/meshes/Link_4.STL |  | LINK4-1 | Origin_Joint3_4 | Axis_Joint3_4 | Joint3_4 | continuous | 0,14 | 0 | 0 | 0 | 0 | -2,2855 | Link_3 | 0 | 0 | -1
Link5 | -0,0810602801359899 | -9,56942858287846E-13 | -0,0211483179569884 | 0 | 0 | 0 | 0,0650308643867626 | 6,37467432310732E-06 | -5,75231297666946E-16 | 5,50791399470628E-17 | 0,000113839820147718 | -4,21084525637092E-17 | 0,000116600795160695 | 0 | 0 | 0 | 0 | 0 | 0 | package://URDF_final/meshes/Link5.STL | 0,752941176470588 | 0,752941176470588 | 0,752941176470588 | 1 | 0 | 0 | 0 | 0 | 0 | 0 | package://URDF_final/meshes/Link5.STL |  | LINK5-1 | Origin_Joint4_5 | Axis_Joint4_5 | Joint4_5 | continuous | -0,14 | 0 | 0,003 | 0 | 0 | 1,8962 | Link_4 | 0 | 0 | -1

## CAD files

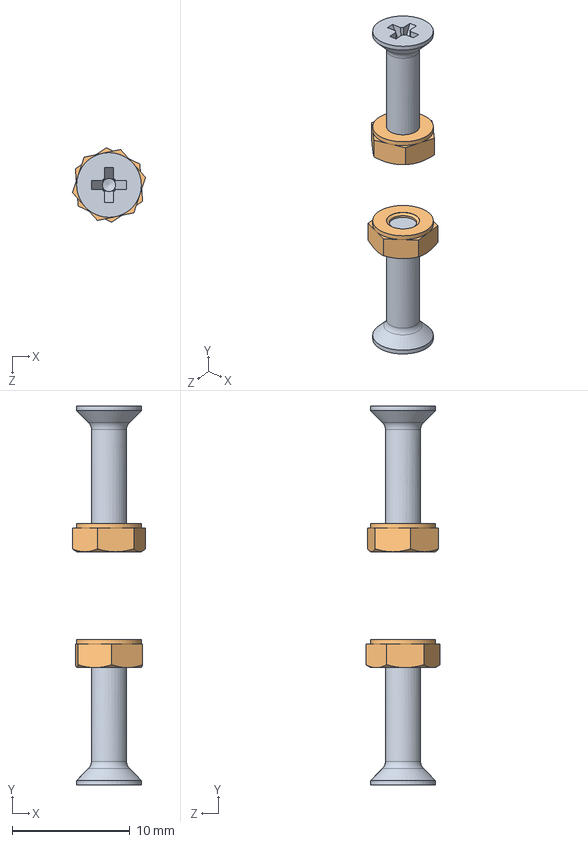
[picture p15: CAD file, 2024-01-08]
CAO Solidworks/Pentographe V2/Assemblage_porte_camera.SLDASM
6.22 x 32.2 x 6.33 mm
countersunk flat head cross recess screw_iso x 2
hex nut style 1 gradeab_iso x 2

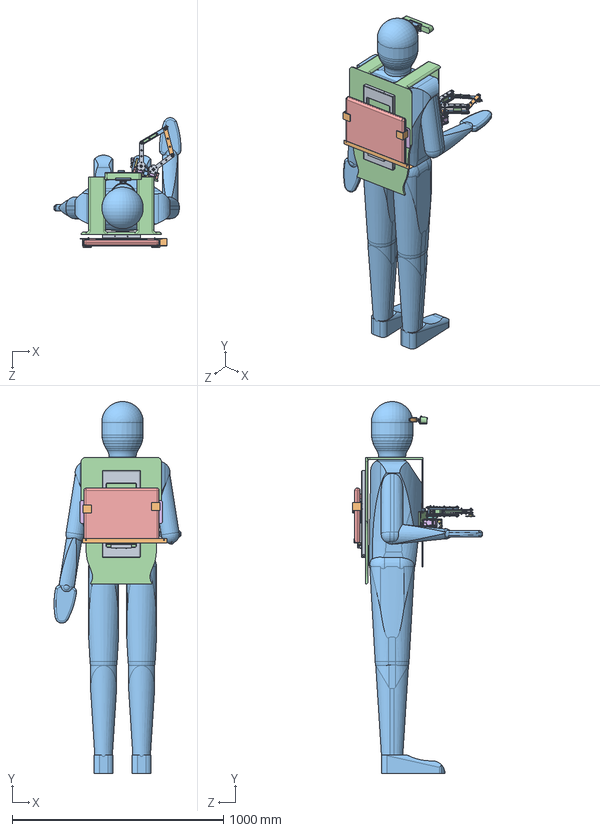
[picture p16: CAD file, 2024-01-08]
CAO Solidworks/Pentographe V2/porte_pc.SLDASM
600.5 x 1760.0 x 613.8 mm
cartable_squelette
rebord
sebastienH
harnais
pc
plaque
egaliseur
pan head cross recess screw_iso x 6
hex thin nut gradeb_iso x 2
Angle x 2
Rail_Harnais
Plaque Verticale
MX-28 SERVO x 2
porte_moteurs_PLA
disque_motor x 2
bras_superieur x 4
bras_3mm_2_etage x 4
bras_5mm x 4
appui_plan x 2
radial ball bearing_68_skf x 10
vis_M4_42mm^Copie de bras_cote_moteur_Assemblage_pento x 4
vis_M4_46mm^Copie de bras_cote_moteur_Assemblage_pento x 2
countersunk flat head cross recess screw_iso x 24
hex nut style 1 gradeab_iso x 35
bras_inferieur_3mm x 2
Bielle_inferieur_2e_etage_3mm x 2
bieille_5mm_inferieur x 2
Copie de entretoise_9mm^Assemblage_pento x 2
Copie de entretoise_16mm^Assemblage_pento x 2
couvercle_poignée
vis_M2_26mm^assemblage_poignee_Assemblage_pento x 2
vis_M4_22mm^Assemblage_pento
plain washer clevis pin grade a_iso
entretoise_12mm^Assemblage_pento
Copie de vis_M4_46mm^Assemblage_pento
Copie (2) de vis_M4_46mm^Assemblage_pento
39281023.prt.stp
JST-B4B-EH-A.PRT.1.stp x 3
JST-B3B-EH-A.PRT.1.stp x 3
Board.stp
attache_casque
porte_camera
ZED2

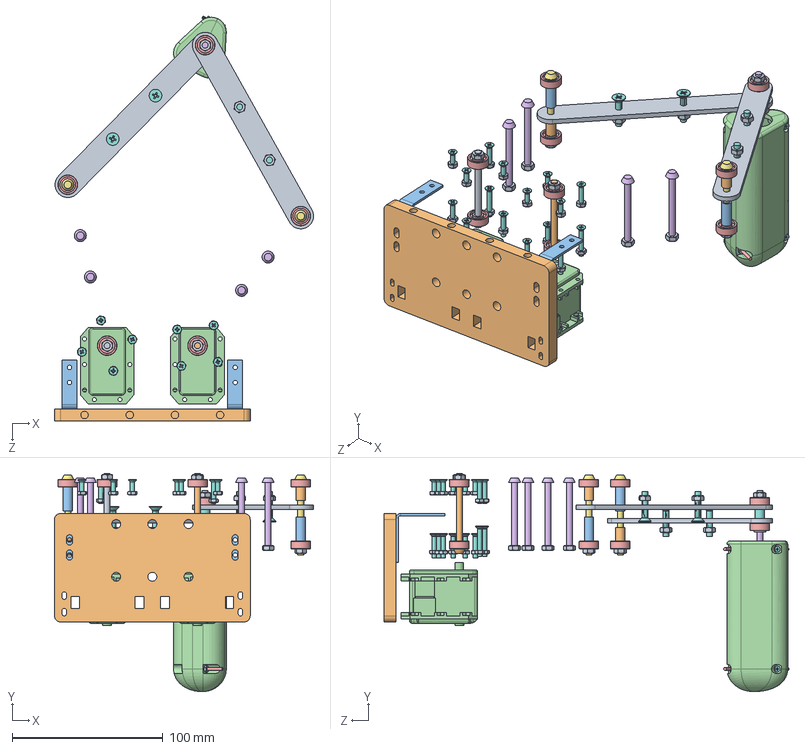
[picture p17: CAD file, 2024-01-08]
CAO Solidworks/Pentographe V2/Assemblage_pento.SLDASM
172.0 x 144.8 x 268.9 mm
Plaque Verticale
MX-28 SERVO x 2
radial ball bearing_68_skf x 10
vis_M4_42mm^Copie de bras_cote_moteur_Assemblage_pento x 4
vis_M4_46mm^Copie de bras_cote_moteur_Assemblage_pento x 2
countersunk flat head cross recess screw_iso x 22
hex nut style 1 gradeab_iso x 33
Bielle_inferieur_2e_etage_3mm x 2
Copie de entretoise_9mm^Assemblage_pento x 2
Copie de entretoise_16mm^Assemblage_pento x 2
poignee^assemblage_poignee_Assemblage_pento
vis_M2_26mm^assemblage_poignee_Assemblage_pento x 2
vis_M4_22mm^Assemblage_pento
plain washer clevis pin grade a_iso
entretoise_12mm^Assemblage_pento
Copie de vis_M4_46mm^Assemblage_pento
Copie (2) de vis_M4_46mm^Assemblage_pento

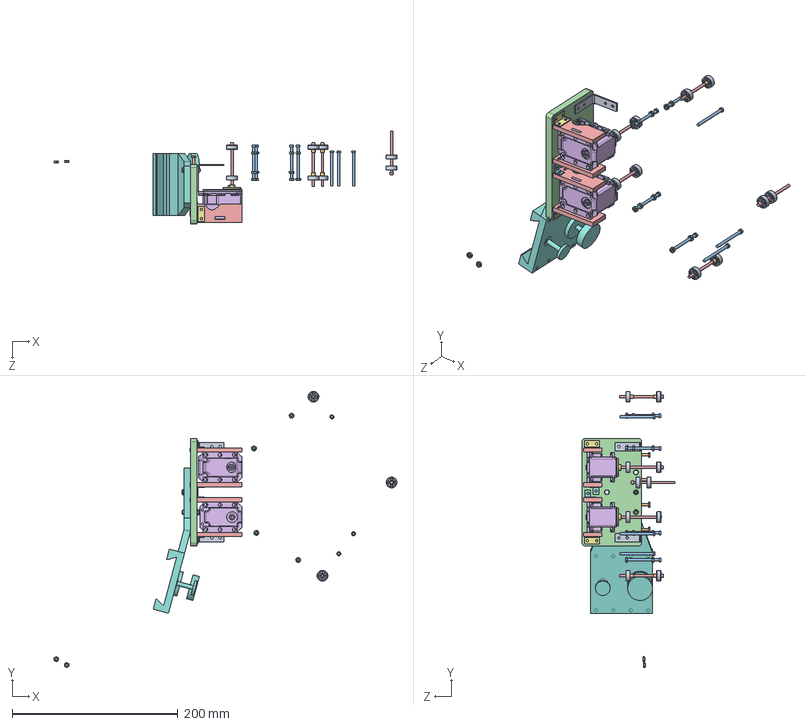
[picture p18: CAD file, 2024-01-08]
CAO Solidworks/Pentographe V2/test_assemblage.SLDASM
413.7 x 333.4 x 112.0 mm
radial ball bearing_68_am x 10
entretoise x 4
vis_M3_40 x 7
hex nut style 1 gradeab_iso x 11
axe x 5
MX-28 SERVO x 3
Disk_driver x 2
Rail_Harnais
pan head cross recess screw_iso_4
hexagon head screw (grades a and b)_as x 5
hexagon nut style 1 (grades a and b) as x 3
Plaque Verticale
Pièce2 x 4
languette_motor x 4
Corniere x 2
Corniere divisé x 2

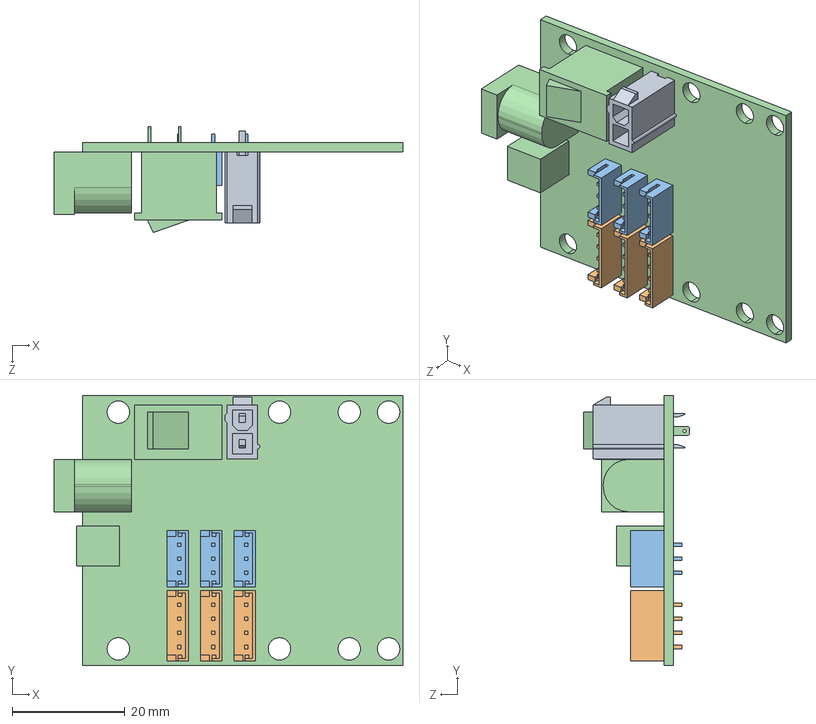
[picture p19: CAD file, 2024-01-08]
CAO Solidworks/Pentographe V2/carte_dynamixel.SLDASM
62.0 x 48.0 x 18.9 mm
39281023.prt.stp
JST-B4B-EH-A.PRT.1.stp x 3
JST-B3B-EH-A.PRT.1.stp x 3
Board.stp

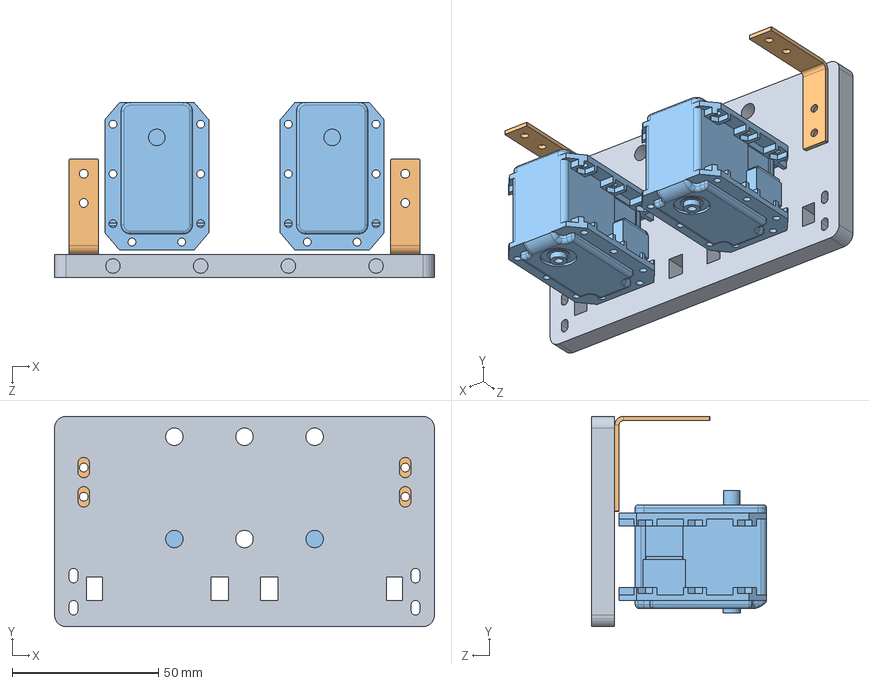
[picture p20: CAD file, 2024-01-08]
CAO Solidworks/Pentographe V2/Fixation Harnais Pento Usinage.SLDASM
130.0 x 72.0 x 60.0 mm
Plaque Verticale
MX-28 SERVO x 2

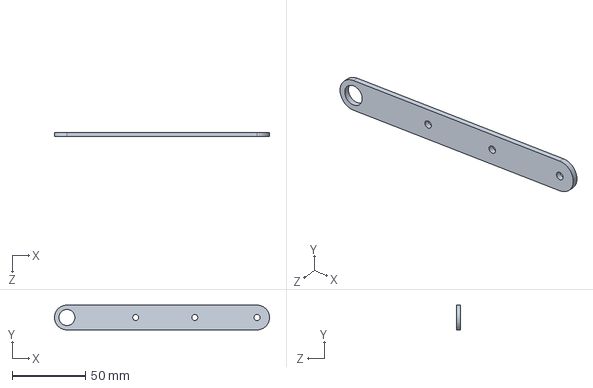
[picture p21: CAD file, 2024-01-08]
CAO Solidworks/Pentographe V2/Bielle_inferieur_2e_etage_3mm.SLDPRT
147.0 x 17.0 x 3.00 mm

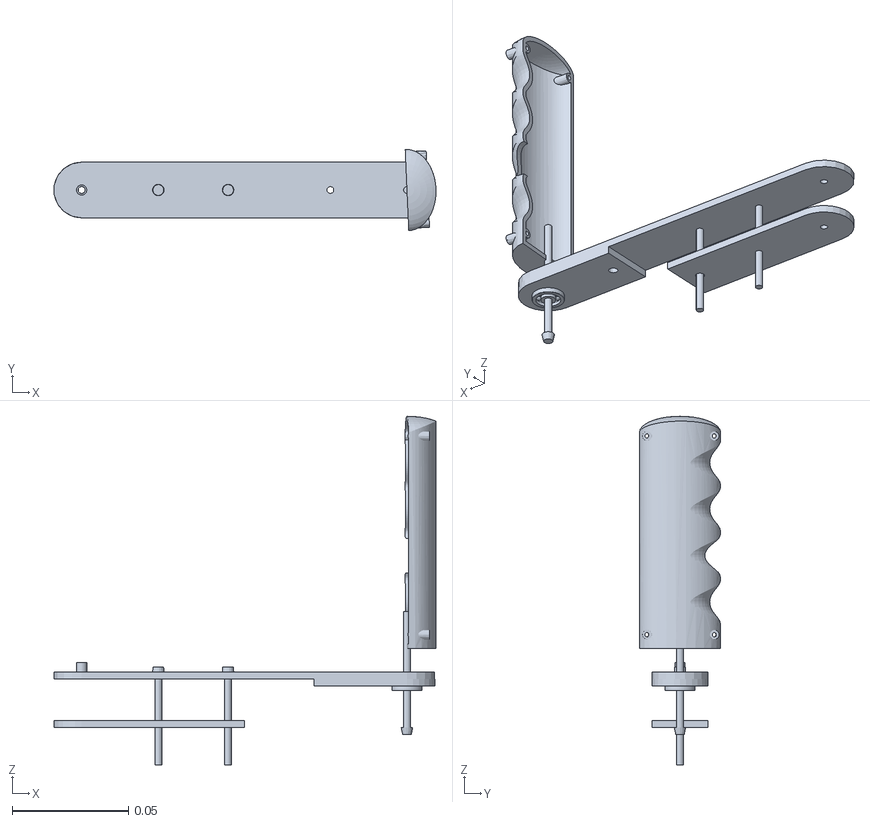
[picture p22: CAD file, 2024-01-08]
dev2_ws/install/two_wheeled_robot/share/two_wheeled_robot/meshes/Link_4.STL
0.164 x 0.035 x 0.15

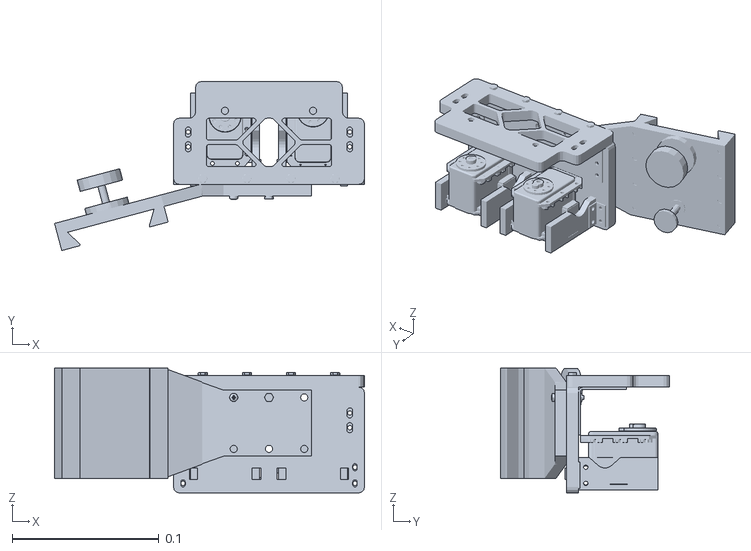
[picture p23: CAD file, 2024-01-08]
dev2_ws/src/two_wheeled_robot/meshes/Link_1.STL
0.211 x 0.115 x 0.085

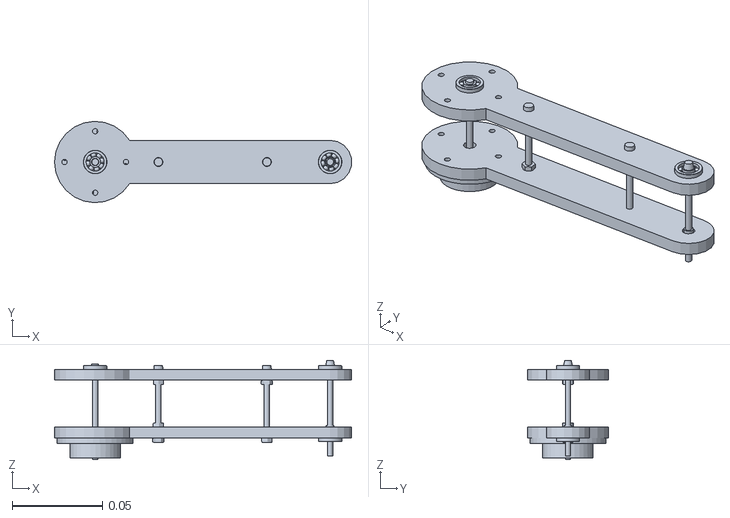
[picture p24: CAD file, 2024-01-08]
Sdw2URDF/URDF_drive/URDF_final/meshes/Link5.STL
0.164 x 0.045 x 0.055

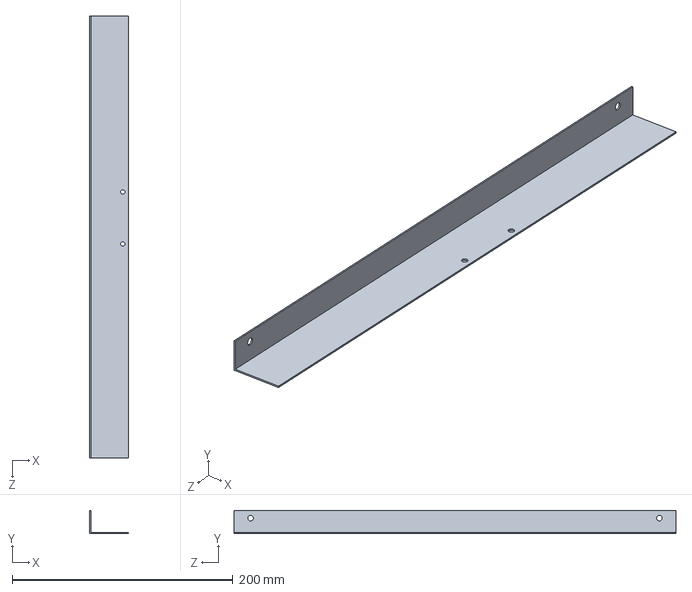
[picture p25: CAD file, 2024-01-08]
CAO Solidworks/Pentographe V2/rebord.SLDPRT
35.0 x 21.0 x 400.0 mm

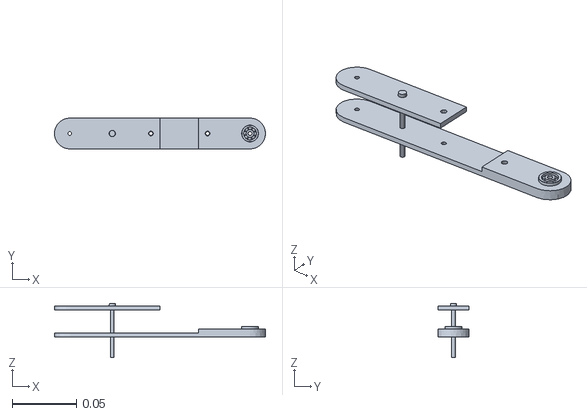
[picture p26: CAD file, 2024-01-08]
dev2_ws/src/two_wheeled_robot/meshes/Link_3.STL
0.164 x 0.024 x 0.042

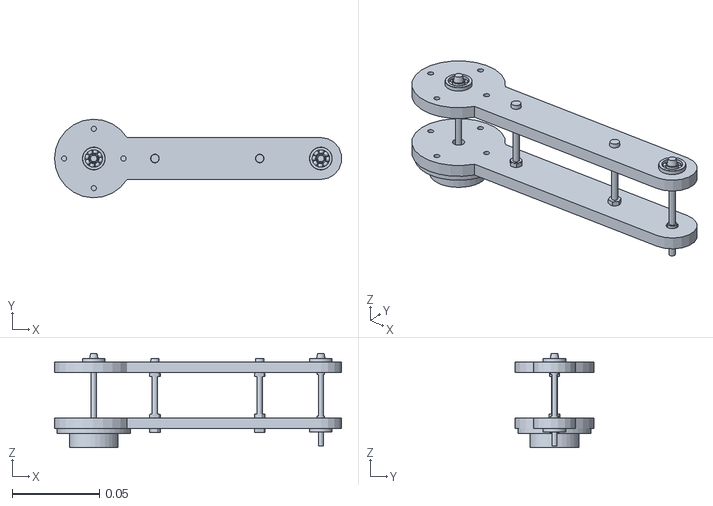
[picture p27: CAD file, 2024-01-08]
Sdw2URDF/URDF_drive/URDF_final/meshes/Link_2.STL
0.164 x 0.045 x 0.054

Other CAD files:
CAO Solidworks/Pentographe V1/100315.SLDPRT
CAO Solidworks/Pentographe V1/Assemblage_poignee.SLDASM
CAO Solidworks/Pentographe V1/Bielle_avec_roulement_depassant - partie haute.SLDPRT
CAO Solidworks/Pentographe V1/Bielle_avec_roulement_depassant - partie basse.SLDPRT
CAO Solidworks/Pentographe V1/Corniere divisé.SLDPRT
CAO Solidworks/Pentographe V1/Corniere.SLDPRT
CAO Solidworks/Pentographe V1/Disk_driver.SLDPRT
CAO Solidworks/Pentographe V1/Fixation Harnais Pento Usinage.SLDASM
CAO Solidworks/Pentographe V1/MX-28 SERVO.SLDPRT
CAO Solidworks/Pentographe V1/Plaque Verticale.SLDPRT
CAO Solidworks/Pentographe V1/Plaque principale.SLDPRT
CAO Solidworks/Pentographe V1/ROBOTIS_U2D2_Power_Hub_Board.SLDASM
CAO Solidworks/Pentographe V1/axe.SLDPRT
CAO Solidworks/Pentographe V1/bielle_2 - partie haute.SLDPRT
CAO Solidworks/Pentographe V1/bielle_2 _partie basse.SLDPRT
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

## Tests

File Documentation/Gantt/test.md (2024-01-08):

```mermaid
gantt
    dateFormat  YYYY-MM-DD
    title       Planning Semestre 1 septembre 2022 - Janvier 2023
    excludes    weekends

    axisFormat %m/%Y

    section Documentation

    Cahier des charges : done, doc1, 2022-09-20,2022-11-01
    Dossier conception préliminaire : done,doc2, after doc1, 2022-11-30
    Dossier conception détaillée : done, doc3,after doc2,2022-12-30

   section Modélisation
   Exploration idées :done, des1, 2022-09-30,2022-10-30
   Simulation/Analyse : done,mod1, after des1 ,20d
   Modélisation SW: done,mod2, after mod1 ,20d
   commande matériel : done,mod3, after mod1 ,20d

   section Protypage
   Conception : done, proto1, after mod3, 2023-01-30

   section Contrôle
   Code ROS2 Moteurs : done, ctrl1, after mod3, 2023-02-01
   Controle Joystick : done, ctrl2, after mod3, 2023-02-01

   section software

   Test SLAM Kinnect ROS1 : done, soft1, after des1, 2023-02-01
   Compréhension SLAM+ROS2 : done, soft2, 2022-11-30, 2023-02-01
   Attente du PC : crit, soft3, 2022-09-30, 2023-01-30

```
```mermaid

gantt
    dateFormat  YYYY-MM-DD
    title       Planning rétro actif Semestre 2 : Fevrier-Juin 2023
    excludes    weekends

    axisFormat %m/%Y

    section Caméra
    Installation SDK + Config PC : done, cam1, 2023-01-30 , 2023-02-15
    STELLA VSLAM : done,cam2, after cam1, 2023-03-01
    Octomap + PCL : done,cam3, after cam2, 2023-03-15
    Tests env : done,cam4, after cam2, 2023-04-20

    section MicroROS+Controle
    Cablage + code sous ROS2 : done, elec1, 2023-03-10, 2023-04-01
    Asservissement: done, elec2, 2023-02-05, 2023-02-10

    section Prototypage V2
    Reconception : done, proto1, 2023-02-01, 2023-03-15
    Assemblage : done, proto2, after proto1, 2023-04-01
    Porte PC si dispo : active, proto3, after proto1, 2023-05-01

    section Navigation
    Compréhension + pistes : done, nav1, 2023-03-01, 2023-03-15
    Implémentation/Interfaçage : active, nav2, after nav1, 2023-05-20

    section Tests globale
    Pilote : milestone, 2023-05-25

    section Documentation
    Rapport : done, doc1, 2023-05-25, 2023-05-30
    Vidéo : done, doc2, 2023-05-25, 2023-05-30

    soutenance 14h: milestone, 2023-06-06

```

```mermaid
gantt
    dateFormat  YYYY-MM-DD
    title       Planning prévisionnel Semestre 2 : Fevrier-Juin 2023
    excludes    weekends

    axisFormat %m/%Y

    section Caméra
    Arrivée PC : crit, cam0, 2023-01-30, 2023-02-01
    Config PC : done, cam1, 2023-01-30 , 2023-02-15
    Slam + Tests : done,cam2, after cam1, 2023-03-10
    Ajout porte caméra : done,cam3, 2023-01-30 , 2023-02-15
    
    section Ajout micro controlleur 
    retour vibreur : done, elec1, 2023-03-10, 2023-04-01

    section Prototypage V2
    Reconception : done, proto1, 2023-02-01, 2023-03-15
    Assemblage : done, proto2, after proto1, 2023-04-01
    Porte PC : active, proto3, 2023-04-01, 2023-04-15

    section Navigation
    Compréhension + pistes : done, nav1, 2023-02-01, 2023-03-01
    Implémentation/Interfaçage : active, nav2, after nav1, 2023-05-20
    
    section Tests
    RDV pilote : crit, test2, 2023-02-15, 2023-03-01
    RDV pilote : crit, test2, 2023-05-15, 2023-05-25

    section Documentation
    Rapport : done, doc1, 2023-05-25, 2023-05-30
    Vidéo : done, doc2, 2023-05-25, 2023-05-30

    soutenance 14h: milestone, 2023-06-06

```

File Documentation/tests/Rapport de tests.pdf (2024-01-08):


# Guidage kinesthésique pour l'assistance aux malvoyants Cybathlon VIS 2024

# Rapport de test

Juin 2023

### Projet Industriel d’année 4 Spécialité Robotique

NGUYEN Victoria | Encadrant : Lilian CARILLET
FU Daniel | Client : Fabien VERITE
SHLYKOVA Olga | Pilote : Sébastien HINDERER

MOREL Théo

Introduction | 3
I- Tests sur les actionneurs et leur contrôle | 4
Test février 2023 | 5
Test Mai 2023 | 6
II- Tests sur l’architecture mécanique | 7
Partie avant | 7
Test février 2023 | 8
Conclusions des tests et piste d’améliorations : | 9
Test Mai 2023 | 11
III- Tests sur l’architecture informatique | 13
Test 1 : algorithme de SLAM | 13
Test 2 : qualité du nuage de point de la ZED 2 et de la cartographie 3D | 14
Conditions des tests | 14
Test 3 : qualité de la projection 2D et possibilité de trouver un chemin manuellement. 15 Test 4 : Algorithme de navigation + Architecture mécanique + Commande moteurs 15

## Introduction

Ce document présente le rapport de tests unitaires et globaux sur nos 2 prototypes du pantographe, dans le cadre du projet industriel de rob 4- 2022/2023, à différents moments du projet.

Nous avons, lors de ce projet, travaillé en bloc :

- L’architecture de commande des actionneurs
- L’architecture mécanique
- L’architecture informatique

Chaque membre de l’équipe a pu travailler sur un ou plusieurs blocs. Afin de tester leur fonctionnement, des tests unitaires ont été fait sur chaque bloc, dans des conditions qui seront décrites. Le but final est, lors du prototype final, réunir chaque bloc afin de vérifier la conformité du prototype entier au cahier des charges et procéder aux tests et à leur validation.

Nous proposons de décrire dans un premier temps les tests unitaires effectués au long du projet sur chacun des 3 blocs. Puis, dans un second temps, nous décrirons les tests menés en situation de Cybathlon, sur le prototype final réunissant les 4 blocs.

# I- Tests sur les actionneurs et leur contrôle

Pour contrôler nos 2 actionneurs et vérifier leur bon fonctionnement, nous avons opté pour des tests manuels avec un joystick (manette).

Pour rappel, nous devons être capable de communiquer des commandes aux moteurs via des topics ROS2. Pour être plus précis, nous nous sommes fixés l’objectif de pouvoir amener l’organe terminal du robot a un endroit précis avec le contrôle des actionneurs via un modèle géométrique indirect.

Objectif des tests :

1. Vérifier que le contrôle fonctionne comme on le souhaite
2. Vérifier que notre vocabulaire kinesthésique choisi soit compréhensible par le pilote
3. Vérifier que le retour kinesthésique soit adapté pour le pilote

Nous avons effectué 2 tests, l’un en février 2023, l’autre en mai 2023, en présence du pilote. Nous avons évalué ces trois critères, sur le barème ci-dessus :

Les moteurs peuvent marcher avec 2 modes :

1. un mode où il faut indiquer la position moteur à atteindre,
2. un mode où on indique la vitesse à incrémenter au position moteur

## Test février 2023

Pour ce premier test, nous avons testé le 1er mode.

Quelques précisions :
Nous avons effectué une interpolation de points entre la position actuelle et la position finale.

Conditions des tests :

En présence du pilote officiel, avec le prototype V1 mécanique du pantographe (voir partie ci-dessous). Harnais comprenant le pantographe seulement.

Critère | Retour et évaluation
1 | La poignée se place bien à la position souhaitée. La précision n’est pas importante, ce qui importe, c’est l’amplitude par rapport à une position d’origine. Très satisfait
2 | Le pilote arrivait à traduire nos consignes en direction horaire, nous permettant de vérifier la cohérence entre le message codée et le message effectivement compris Très satisfait
3 | Asservissement en position, causant ainsi des salves de mouvements, rendant le mouvement non fluide, et perturbant le message : l’effecteur atteignait la position demandée avec un trajet brusque. Insatisfait

Ainsi, les tests ont montré un code fonctionnel grâce à un joystick, et un retour kinesthésique sur la bonne voie. Cependant, il n’est pas encore totalement adapté pour le pilote, ce qui induit une fonction contrainte du cahier des charges qui n’est pas encore totalement remplie. (FC2)

## Test Mai 2023

Pour ce premier test, nous avons testé le second mode.

Quelques précisions :

Nous avons effectué un asservissement en récupérant la position actuelle que l’on a comparé avec la “goal” position. Nous avions donné une vitesse constante à incrémenter au position moteur

Conditions des tests :

En présence du pilote officiel, avec le prototype V2 mécanique du pantographe (voir partie ci-dessous ). Harnais comprenant le pantographe seulement, ainsi que l’ordinateur sur le dos, et la caméra sur la tête.
Une piste recrée a été faite, afin de tester ce retour en situation réelle.

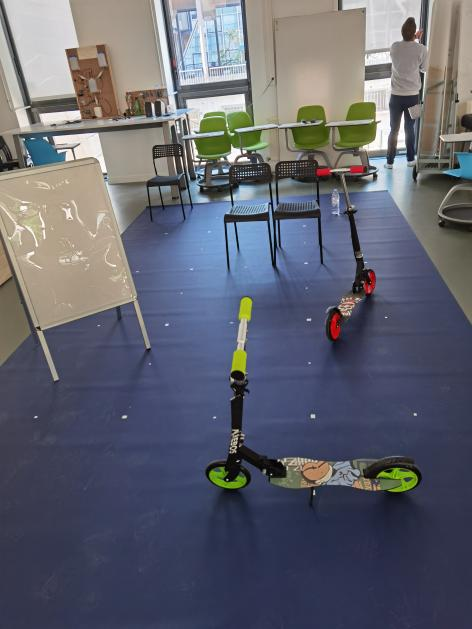
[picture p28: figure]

piste de l’épreuve SideWalk

Critère | Retour et évaluation
1 | Très satisfait
2 | Le pilote arrive se déplacer ou l’on souhaite, grâce au retour kinesthésique. Aucun obstacle n’a été touché. Très satisfait
3 | Le retour est fluide, et un passage par zéro permet au pilote d’avoir un référentiel fixe par rapport a son buste. On ne perd ainsi pas l’information. Très satisfait

Au travers de ces deux tests, notre chemin de réflexion, en collaboration avec le pilote lui-même, a permis de voir le pilote en action sur une première piste. Le cahier des charges est satisfait.

# II- Tests sur l’architecture mécanique

La conception mécanique se porte intégralement sur le pilote. Elle se divise en 2 sous blocs :

- La partie avant, qui constitue l’architecture mécanique motorisé situé à l’avant du harnais : le pantographe
- La partie arrière, capable de porter le pc portable

## Partie avant

Il y a eu 2 prototypes du pantographe. En effet, nous avons fait une première salve de tests à mi semestre , du prototype mécanique. Selon les retours du pilote explicités ci-dessous, nous avons procédé à des améliorations. Les deux prototypes et leurs tests sont explicités ci-dessous.

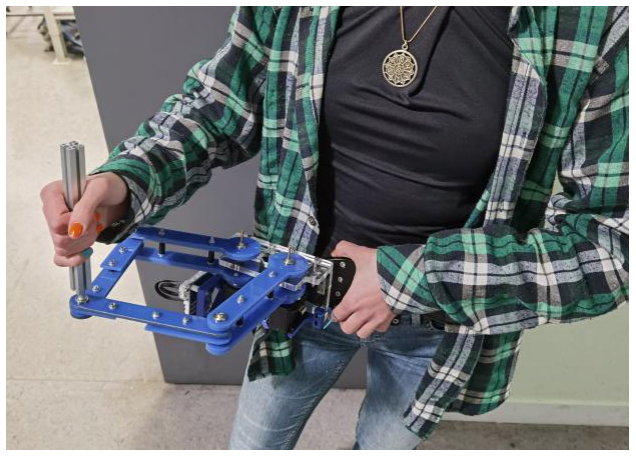
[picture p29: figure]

Finalisation du 1er prototype

## Test février 2023

Un premier test a été réalisé en février 2023, en présence de Sébastien Hinderer, le pilote. Nous avions pour but de tester plusieurs facteurs compris dans des fonctions du cahier des charges.

Objectif des tests :

1. vérifier la portabilité du prototype du pantographe sur le pilote
2. Vérifier son confort au niveau des bras pour le pilote, le temps de la course
3. Vérifier la rigidité mécanique du prototype en situation fictive
4. Confronter notre estimation de l’espace de travail avec celui réellement besoin

L’objectif était également d’avoir des retours et des remarques que seul Sébastien pouvait nous indiquer.

Conditions des tests :

Similaire à la partie précédente, celle du premier test de février : seul le pantographe était porté sur le harnais. Pas encore autonome : les moteurs restent branchés au secteur et au PC.

Critère | Retour et évaluation
1 | Le pilote a pu rester une trentaine de minutes avec le prototype. Celui-ci s'accroche bien au harnais, et est relativement facilement enfilable grâce à une aide extérieure. Le prototype, relativement a d’autre prototype antérieur, est plus léger et moins encombrant Très satisfait
2 | La poignée du prototype V1 était retournée vers le haut, obligeant le pilote a lever le coude. Après 20 minutes de tests, cela lui fatiguait les muscles. Le pilote avait à sa disposition une poignée ergonomique adapté à la prise, avec un pouce devant être placé sur le haut de la poignée. Le pilote préfère avoir un forme sans ergonomie et se placer ou il le souhaite Insatisfait
3 | On a pu constater que le robot manquait de rigidité au niveau des liaisons pivots, à cause d’appui plan trop faible. On perd ainsi de l’information kinesthésique. Insatisfait
4 | L’espace de travail peut être réduit en avant du pilote. Cela n’est pas gênant, mais nous pouvons encore gagner en encombrement (notamment pour la caméra) satisfait

### Conclusions des tests et piste d’améliorations :

Le test consiste surtout à valider le retour kinesthésique , de la part du client et du pilote, en situation de cybathlon. Des points, relevés par le pilote et le client, ont été soulevés, et feront l’objet d’une amélioration d'ici la seconde salve de tests.

Ajouts suggérés par le pilote :

- Un retour sonore peut être envisagé, notamment sur le type de l’obstacle présent à proximité immédiate du pilote.

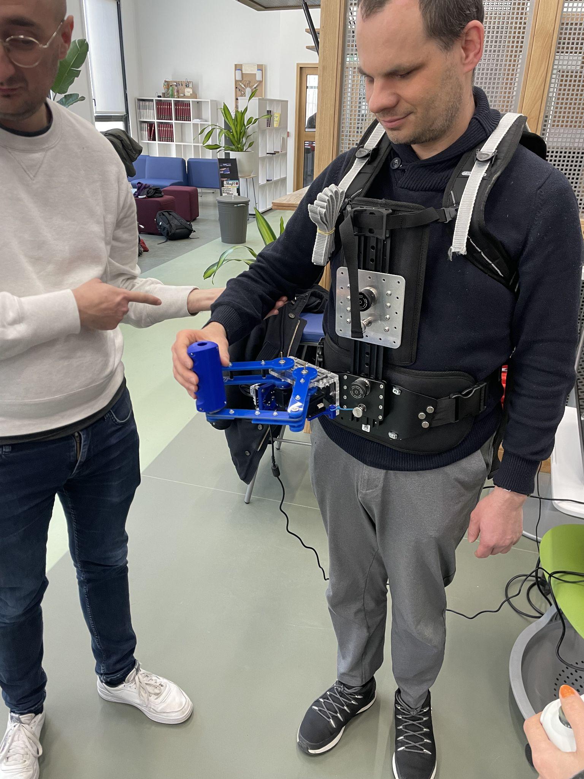
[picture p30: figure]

Le client et le pilote

## Test Mai 2023

Un second test a été réalisé en mai 2023, en présence de Sébastien Hinderer, le pilote. Des améliorations et ajouts mécaniques sont à noter .

- Notamment, le porte PC décrit précédemment, allant à l’arrière du pilote.
- Le pantographe a été refait, changeant les appuis et les dimensions des bielles.

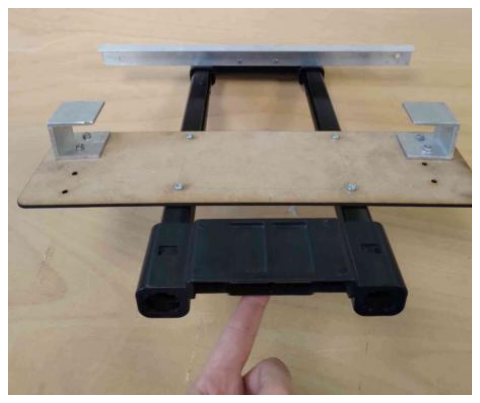
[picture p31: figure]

Conditions des tests :

Au fablab, avec le porte PC en plus, rajoutant ainsi 2,5 kg sur le harnais. Une piste factice.

Critère | Retour et évaluation
1 | Le pilote arrive à mettre le harnais. Ce dernier fait que les appuis sont faits au niveau de la taille, et non pas des épaules. Très satisfait
2 | La poignée a été changée, la préhension est plus agréable pour le pilote. L’orientation vers le bas fatigue moins l’avant bras. Certains câbles gênent le mouvement. satisfait
3 | Le pantographe est stable à tous les niveaux. Très satisfait
4 | Très satisfait

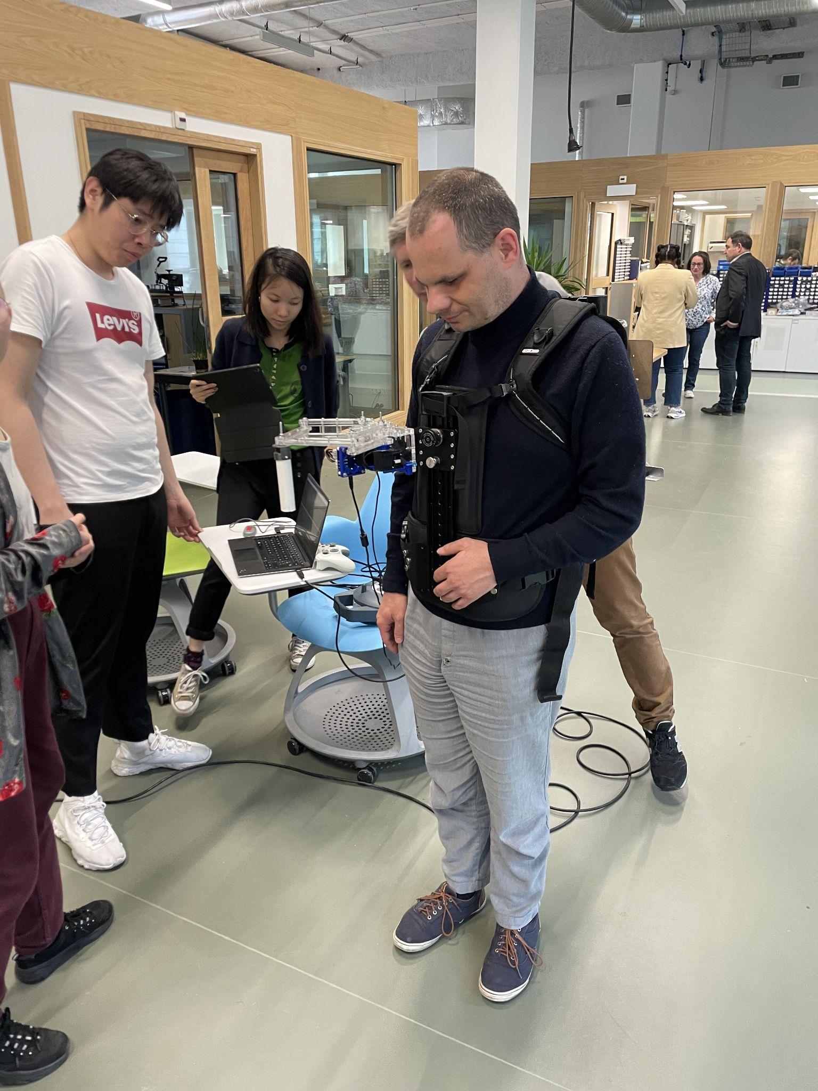
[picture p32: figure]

# III- Tests sur l’architecture informatique

Cette partie présente les tests unitaires sur chaque fonctionnalité utilisée de la caméra. Les conditions des tests sont décrites, et leurs résultats.

## Test 1 : algorithme de SLAM

Afin de choisir l’outil le plus approprié pour faire notre cartographie 3D puis 2D, nous avons fait des tests préliminaires

Nous avons comparé le résultat du SLAM obtenu via le SDK de la ZED2, avec Stella VSLAM (https://github.com/stella-cv/stella_vslam) .

Résultat de la comparaison des deux algorithmes de SLAM :

SLAM de la ZED2 | Stella VSLAM
+ Rapidité d'exécution + Déjà intégré dans la sdk , donc évite une surcharge de calcul non nécessaire pour l’ordinateur - L'algorithme de Stereolabs est statique : un obstacle amovible reste toujours visible sur ses positions précédentes. | + Construction d’un carte dynamique : un obstacle amovible est amovible sur la carte 3D aussi - Local a Pangolin Viewer : on ne peut pas l’observer sur un topic ROS. - Difficulté à extraire le nuage de points via ROS - Stella VSLAM n’est pas destiné à ROS

Ce test a surtout servi à comparer deux algorithmes de SLAM et observer les performances de chacun. Stella SLAM est par ailleurs arrivée comme première option pour le SLAM, et nous avons vu tard le SLAM venant de la ZED 2.

Le résultat de ce test, pour des raisons de performances évidentes pour l’ordinateur, et pour la compétition chronométrée, nous optons pour le SLAM déjà intégré dans le SDK de la ZED 2.

## Test 2 : qualité du nuage de point de la ZED 2 et de la cartographie 3D

Le but du test est d’évaluer la qualité du nuage de points dans un environnement délimité, et d’observer et régler l’influence des différents paramètres possible dans le fichier de configuration de la ZED 2 :

zed-ros2-wrapper/zed wrapper/config/common.yaml

Ces tests se sont fait dans plusieurs environnements.

Conditions des tests

Test des performances de la ZED 2 dans différents environnements et avec différentes luminosités.

- La caméra est attachée à une visière de travail, destinée à être posée sur la tête du pilote.
- une calibration au sol est préalablement effectuée
- Les tests sont majoritairement effectués dans une salle de classe standard, ainsi que dans un couloir vide. Éclairage naturel.

Les résultats des tests se sont traduits par un ajustement des paramètres de la ZED 2.

Numéro | Problème et Paramètres correspondant | Solution choisie
1 | Les dimensions de la piste sont connues. Nous pouvons cropper le nuage de points de la ZED2, et limiter l’espace de vision au strict nécessaire (pas de plafond , ni de sol projeté) | z: [0.2 , 1.8] y : [-1.5,1.5] x : [0,5]
2 | Pour avoir un nuage de points “fin”, on agit sur la résolution | 5cm pour une cellule
3 | Un algorithme causant la création d’un nuage de points d’une taille très importante qui cause potentiellement l’arrêt de la mise à jour. Changer l’allocation de mémoire | Prendre une mémoire par défaut plus importante en multiple de 2

Ainsi, en changeant et en ajustant les paramètres direct de la ZED 2, on limite les opérations de traitements de filtrage, qui ralentit l’algorithme.

## Test 3 : qualité de la projection 2D et possibilité de trouver un

chemin manuellement.

Objectif :
Nous avons une caméra ZED 2, reliée à l’ordinateur situé dans le dos du pilote. Nous devons pouvoir donner les informations venant de la caméra en entrée d’un algorithme de navigation. Le but est d’avoir en sortie d’un nœud une projection 2D du point cloud qui soit exploitable pour de la navigation, parfois délicate car passages étroits possibles selon le nombre d’obstacles.

Input : Un environnement de taille connue, avec des obstacles.

Output : Une cartographie 2D de l’environnement, représentant la probabilités d’occupation de chaque unité. Type de message : nav_msgs/OccupancyGrid.

Il nous faut tester et ajuster :

- La qualité de l’occupancy grid : elle ne doit pas être clairsemée et ne pas avoir de bruit/parasites que ne correspondent pas des obstacles réels.
- Ajouter des délimitations avec une marge à définir

Conditions des tests

- FabLab de Sorbonne Université, Esclangon
- Présence du pilote officiel, des membres de l’ISIR et des encadrants Polytech
- Une piste recréé via un tapis aux dimensions, remplie d’obstacles
- Eclairage via lumière du jour (14h)

Résultats des tests :

Une carte occupancy grid qui représente bien la réalité. Attention au reflet, qui perturbe quelque fois la représentation.

## Test 4 : Algorithme de navigation + Architecture mécanique + Commande moteurs

L’algorithme de navigation n’a pas fonctionné dans la situation réelle : problème hardware (batterie externe non adaptée) et software. L’algorithme n’est pas encore parfaitement fonctionnel.
Algorithme optimal dans la théorie mais un peu trop lent en pratique, il transmet l’information au pilote un peu tardivement.

Position de départ fixe, ce qui peut poser certains problèmes de précision du pilote que l’on initie au milieu de la piste alors qu’il sera sûrement un peu décalé dans la pratique.

Lorsque la position finale est située sur un obstacle, il ne trouve aucun moyen de l’atteindre ni de s’en approcher.
De même, le décalage dû à la position fixe peut poser problème sur la position initiale du pilote et peut le faire démarrer sur un obstacle, ce qui ne trouvera aucun trajet possible => Corrigé grâce à un offset

On ne peut pour l’instant pas identifier si l’objet est au sol ou s’il est en l’air, de plus nous n’avons aucune information sur la taille des objets.

Remarques :
- Pas de bouton d’arrêt d’urgence mis en place actuellement par manque de temps. Il sera nécessaire le jour de la compétition.

Le pilote souhaite néanmoins un bouton côté main gauche qui pourra être activé à tout moment. Le bouton serait préférablement un interrupteur bloquant plutôt qu’un bouton d'arrêt d’urgence classique.

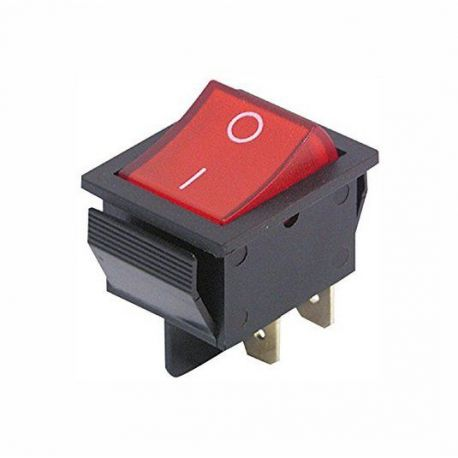
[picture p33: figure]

## Conclusion

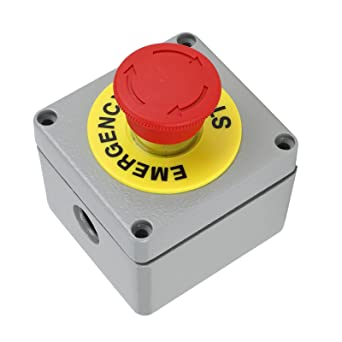
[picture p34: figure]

Nos tests sont dans la majorité concluants : tout l’algorithme fonctionne via ROS2 comme voulu. Le pilote est quasi autonome dans son trajet : il manquera seulement une batterie pour les moteurs qui sera facilement obtenue par la suite.
Les fonctions du cahier des charges (voir section Documentation) sont remplies ou partiellement remplies, et toutes nos remarques et réflexions sont consignés dans la documentation.

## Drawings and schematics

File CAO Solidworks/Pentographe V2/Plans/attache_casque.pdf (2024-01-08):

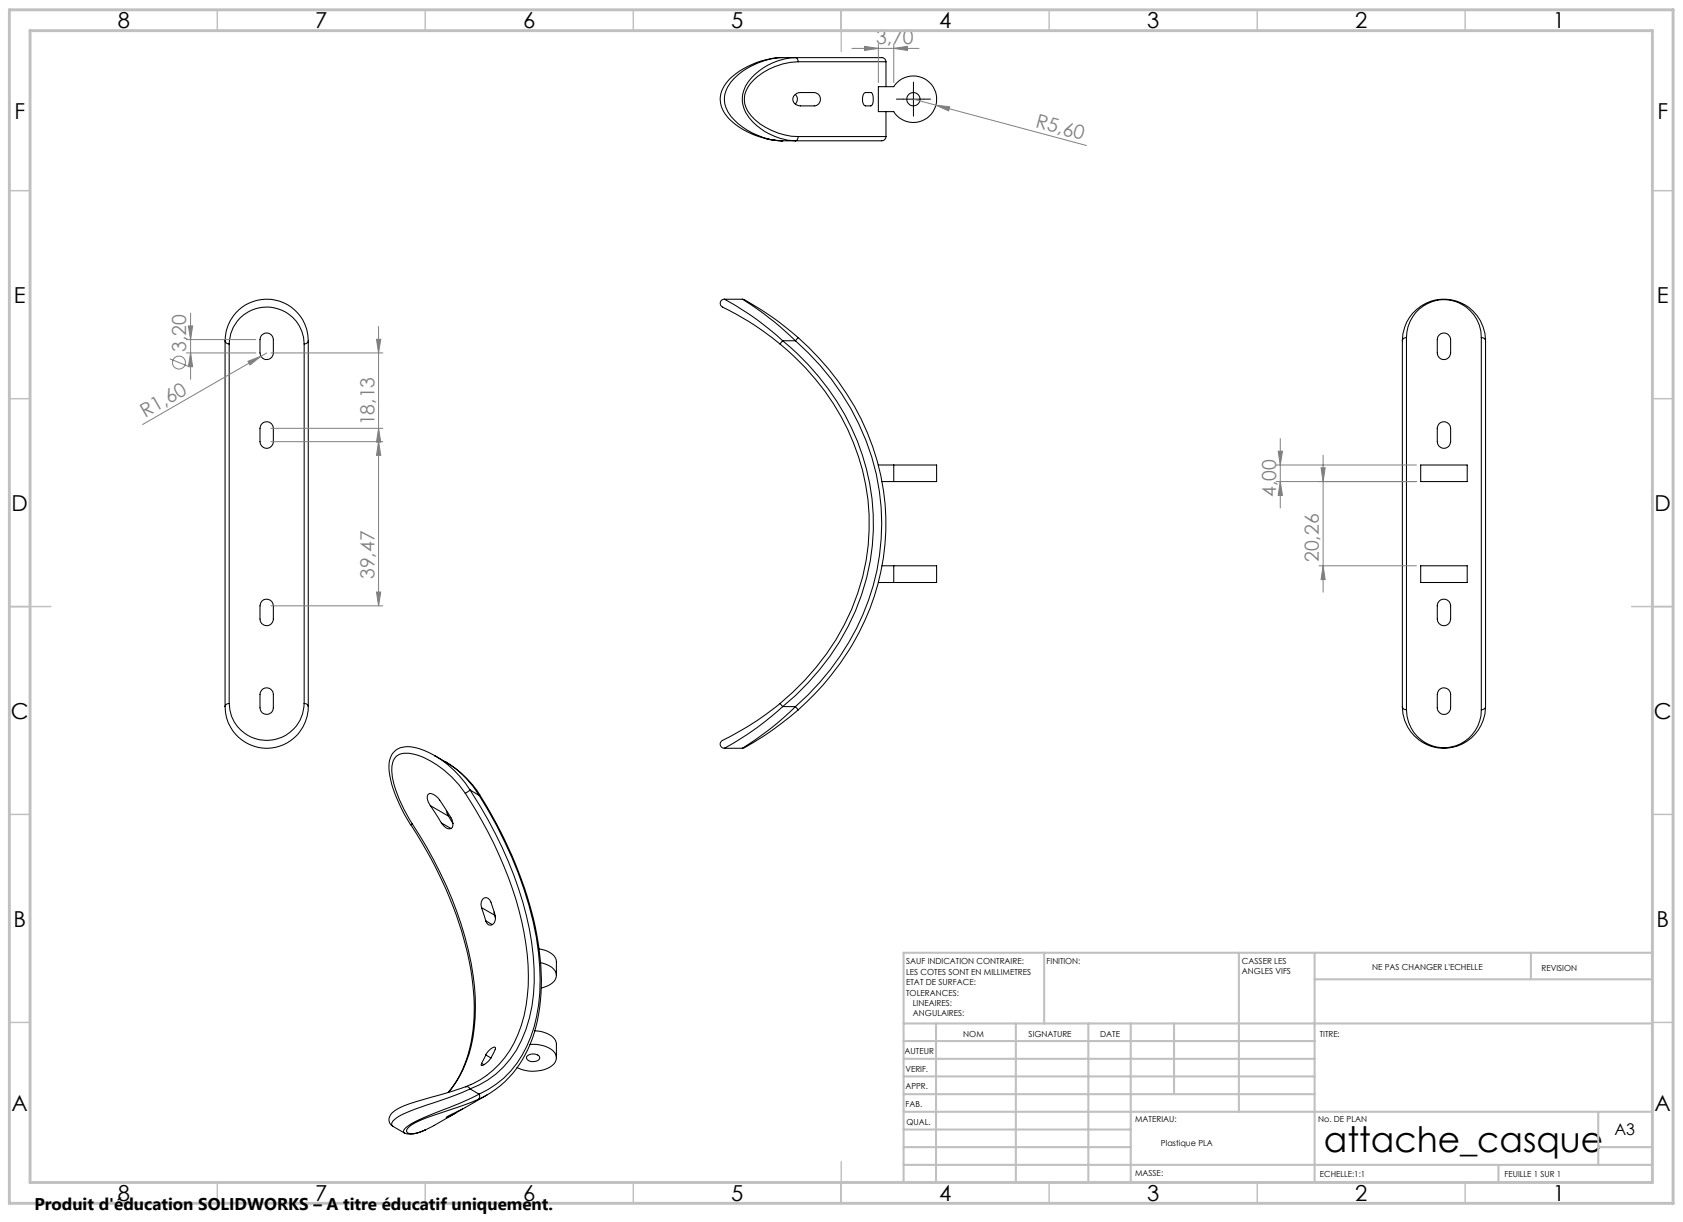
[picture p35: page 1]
FINITION:; CASSER LES; ANGLES VIFS; NE PAS CHANGER L'ECHELLE; REVISION; ECHELLE:1:1; FEUILLE 1 SUR 1

SAUF INDICATION CONTRAIRE:
LES COTES SONT EN MILLIMETRES
ETAT DE SURFACE:
TOLERANCES:
LINEAIRES:
ANGULAIRES:

NOM | SIGNATURE | DATE | | | | TITRE:

AUTEUR
VERIF.
APPR.
FAB.
QUAL. | | | | MATERIAU: Plastique PLA | No. DE PLAN attache_casque | A3

Produit d'éducation SOLIDWORKS – A titre éducatif uniquement.

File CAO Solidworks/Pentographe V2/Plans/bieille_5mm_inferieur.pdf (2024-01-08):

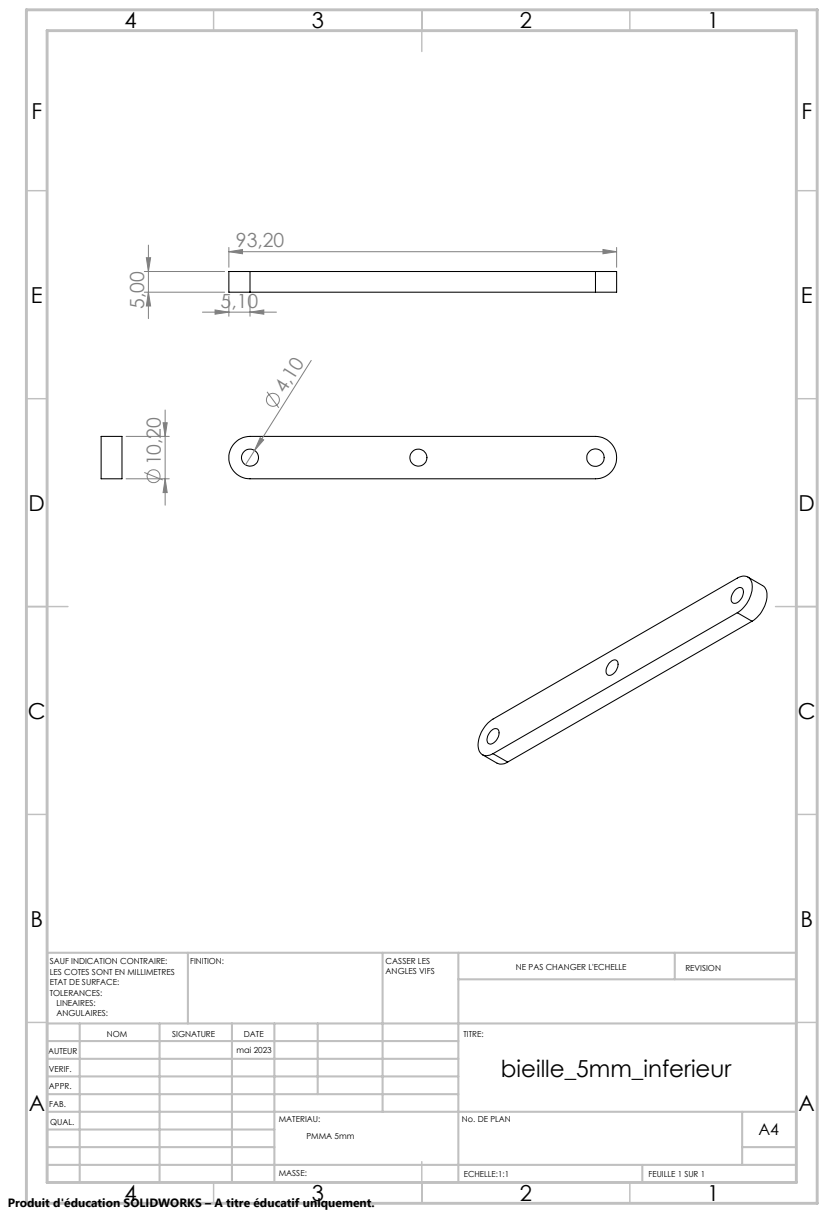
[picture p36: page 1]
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

SAUF INDICATION CONTRAIRE:
LES COTES SONT EN MILLIMETRES
ETAT DE SURFACE:
TOLERANCES:
LINEAIRES:
ANGULAIRES:

NOM | SIGNATURE | DATE | | | | TITRE:

AUTEUR | | | | | | | bieille_5mm_inferieur mai 2023
VERIF.
APPR.
FAB.
QUAL. | | | | MATERIAU: PMMA 5mm | No. DE PLAN | A4

Produit d'éducation SOLIDWORKS – A titre éducatif uniquement.

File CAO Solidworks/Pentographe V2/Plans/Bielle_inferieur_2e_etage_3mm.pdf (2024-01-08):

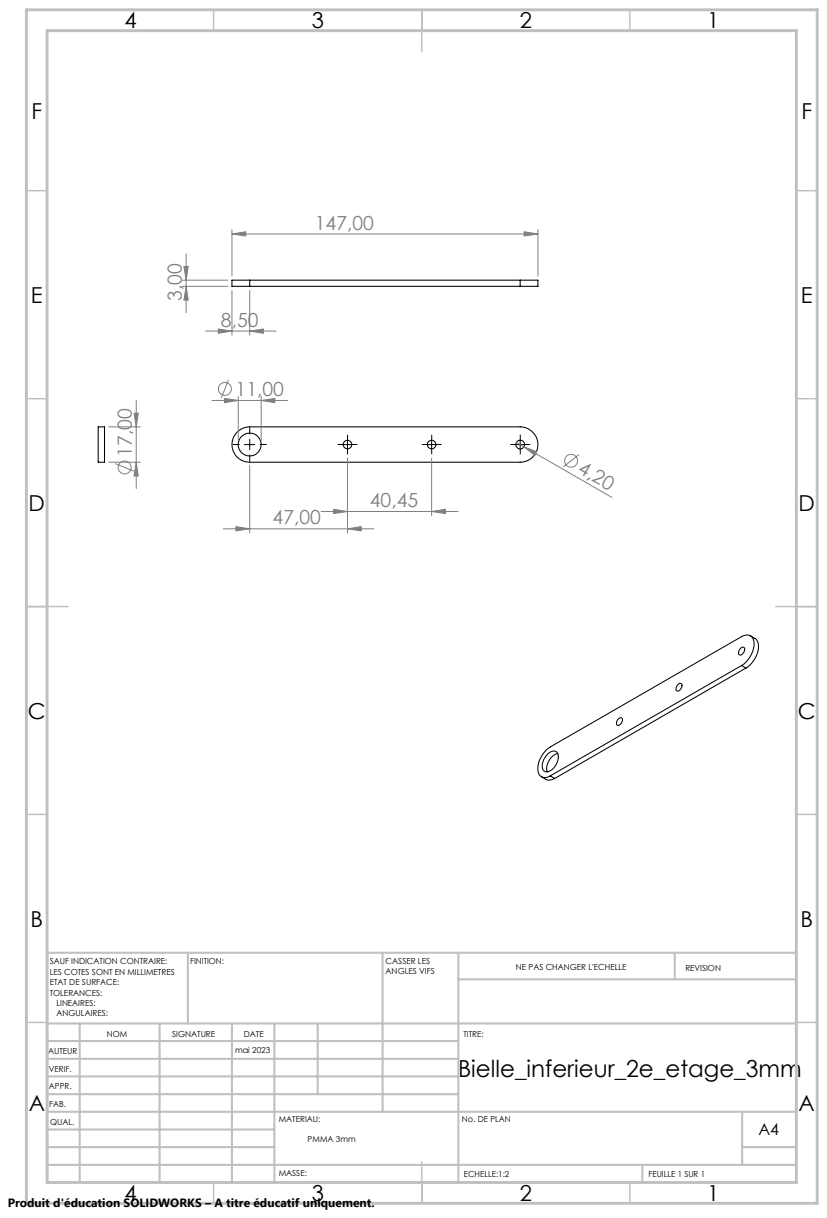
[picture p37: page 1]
FINITION:; CASSER LES; ANGLES VIFS; NE PAS CHANGER L'ECHELLE; REVISION; ECHELLE:1:2; FEUILLE 1 SUR 1

SAUF INDICATION CONTRAIRE:
LES COTES SONT EN MILLIMETRES
ETAT DE SURFACE:
TOLERANCES:
LINEAIRES:
ANGULAIRES:

NOM | SIGNATURE | DATE | | | | TITRE: Bielle_inferieur_2e_etage_3mm

AUTEUR | | | mai 2023
VERIF.
APPR.
FAB.
QUAL. | | | | MATERIAU: PMMA 3mm | No. DE PLAN | A4

Produit d'éducation SOLIDWORKS – A titre éducatif uniquement.

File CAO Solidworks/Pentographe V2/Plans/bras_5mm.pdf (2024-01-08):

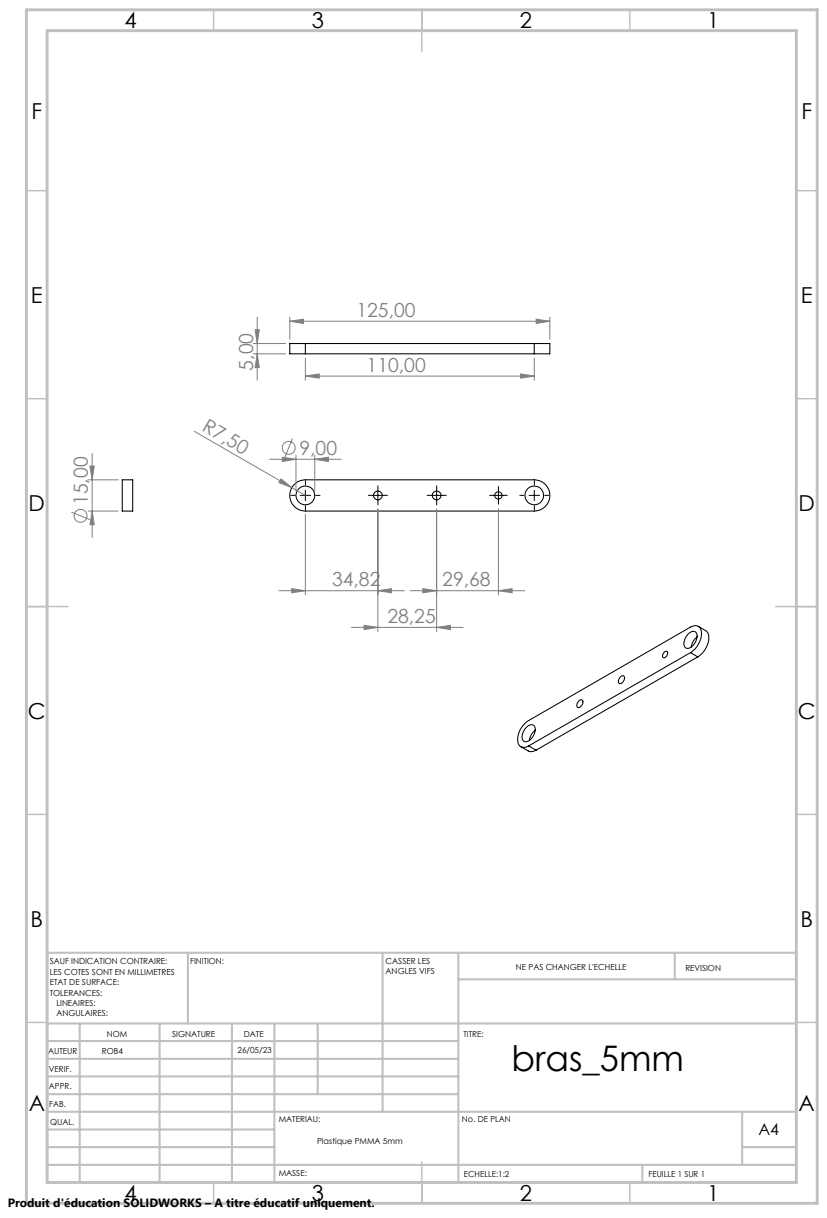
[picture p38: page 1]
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

SAUF INDICATION CONTRAIRE:
LES COTES SONT EN MILLIMETRES
ETAT DE SURFACE:
TOLERANCES:
LINEAIRES:
ANGULAIRES:

AUTEUR | | | 26/05/23 | | | | bras_5mm ROB4

NOM | SIGNATURE | DATE | | | | TITRE:

VERIF.
APPR.
FAB.
QUAL. | | | | MATERIAU: Plastique PMMA 5mm | No. DE PLAN | A4

Produit d'éducation SOLIDWORKS – A titre éducatif uniquement.

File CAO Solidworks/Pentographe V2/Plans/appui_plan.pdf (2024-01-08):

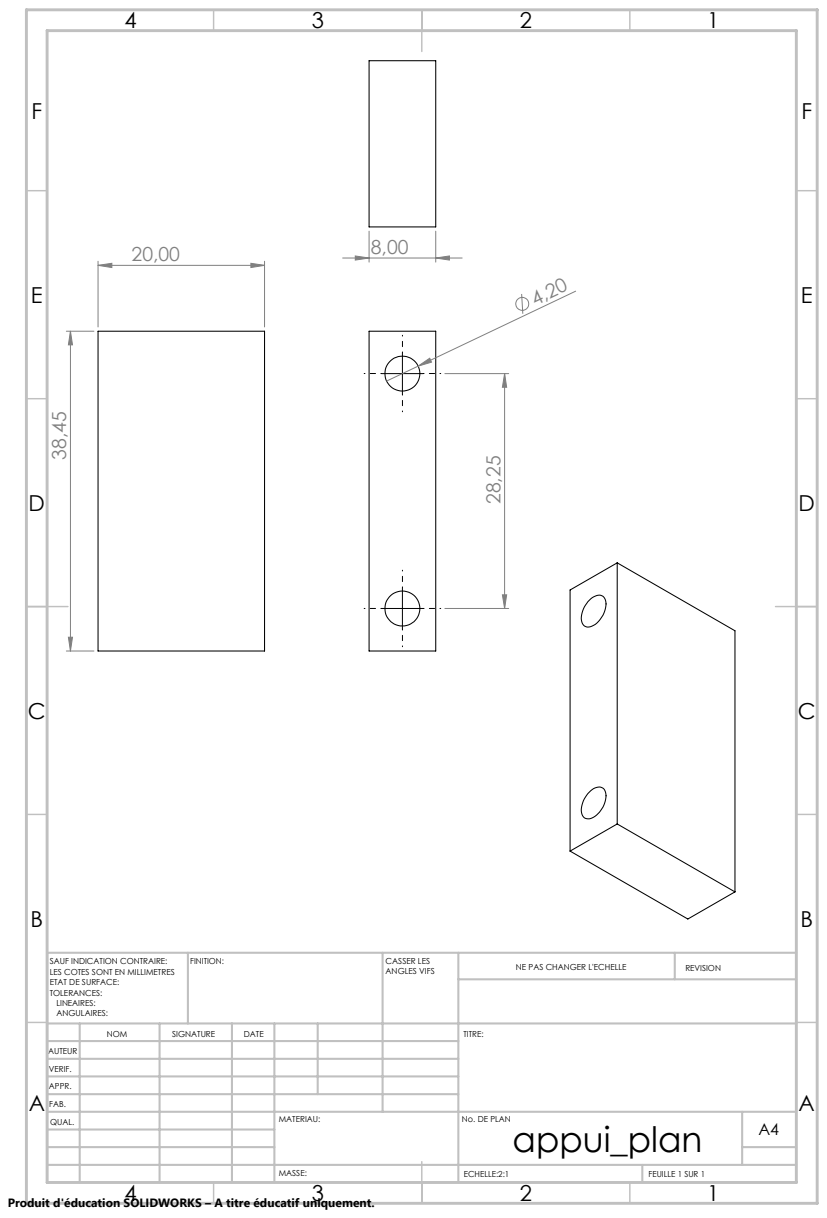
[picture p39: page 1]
FINITION:; CASSER LES; ANGLES VIFS; NE PAS CHANGER L'ECHELLE; REVISION; ECHELLE:2:1; FEUILLE 1 SUR 1

SAUF INDICATION CONTRAIRE:
LES COTES SONT EN MILLIMETRES
ETAT DE SURFACE:
TOLERANCES:
LINEAIRES:
ANGULAIRES:

NOM | SIGNATURE | DATE | | | | TITRE:

AUTEUR
VERIF.
APPR.
FAB.
QUAL. | | | | MATERIAU: | No. DE PLAN appui_plan | A4

Produit d'éducation SOLIDWORKS – A titre éducatif uniquement.

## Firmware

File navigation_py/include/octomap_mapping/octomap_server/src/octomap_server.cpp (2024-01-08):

// Copyright 2010-2013, A. Hornung, University of Freiburg. All rights reserved.
//
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
//    * Redistributions of source code must retain the above copyright
//      notice, this list of conditions and the following disclaimer.
//
//    * Redistributions in binary form must reproduce the above copyright
//      notice, this list of conditions and the following disclaimer in the
//      documentation and/or other materials provided with the distribution.
//Pages
//    * Neither the name of the Willow Garage nor the names of its
//      contributors may be used to endorse or promote products derived from
//      this software without specific prior written permission.
//
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

/*

Modified by Victoria N.
14 April 2023 10h

*/


#include <octomap_server/octomap_server.hpp>

#include <tf2_eigen/tf2_eigen.h>
#include <tf2_geometry_msgs/tf2_geometry_msgs.h>

#include <algorithm>
#include <limits>
#include <memory>
#include <string>
#include <vector>

#include <pcl/filters/statistical_outlier_removal.h>


#define LIMIT_X 5.50
#define LIMIT_Y 1.50

namespace
{
  template <typename T>
  bool update_param(const std::vector<rclcpp::Parameter> &p, const std::string &name, T &value)
  {
    auto it = std::find_if(
        p.cbegin(), p.cend(), [&name](const rclcpp::Parameter &parameter)
        { return parameter.get_name() == name; });
    if (it != p.cend())
    {
      value = it->template get_value<T>();
      return true;
    }
    return false;
  }
} // namespace

namespace octomap_server
{
OctomapServer::OctomapServer(const rclcpp::NodeOptions & node_options)
: Node("octomap_server", node_options)
{
  using std::placeholders::_1;
  using std::placeholders::_2;

  std::cout<<"Initializing OctomapServer"<<std::endl;
  // avec get_logger
  RCLCPP_WARN(get_logger(), "Initialisation du noeud OctomapServer");
  
  

  world_frame_id_ = declare_parameter("frame_id", "map");
  base_frame_id_ = declare_parameter("base_frame_id", "base_footprint");
  use_height_map_ = declare_parameter("use_height_map", false);
  use_colored_map_ = declare_parameter("colored_map", false);
  color_factor_ = declare_parameter("color_factor", 0.8);

  point_cloud_min_x_ = declare_parameter("point_cloud_min_x", -std::numeric_limits<double>::max());
  point_cloud_max_x_ = declare_parameter("point_cloud_max_x", std::numeric_limits<double>::max());
  point_cloud_min_y_ = declare_parameter("point_cloud_min_y", -std::numeric_limits<double>::max());
  point_cloud_max_y_ = declare_parameter("point_cloud_max_y", std::numeric_limits<double>::max());
  {
    rcl_interfaces::msg::ParameterDescriptor point_cloud_min_z_desc;
    point_cloud_min_z_desc.description = "Minimum height of points to consider for insertion";
    rcl_interfaces::msg::FloatingPointRange point_cloud_min_z_range;
    point_cloud_min_z_range.from_value = -100.0;
    point_cloud_min_z_range.to_value = 100.0;
    point_cloud_min_z_desc.floating_point_range.push_back(point_cloud_min_z_range);
    point_cloud_min_z_ = declare_parameter("point_cloud_min_z", -100.0, point_cloud_min_z_desc);
  }
  {
    rcl_interfaces::msg::ParameterDescriptor point_cloud_max_z_desc;
    point_cloud_max_z_desc.description = "Maximum height of points to consider for insertion";
    rcl_interfaces::msg::FloatingPointRange point_cloud_max_z_range;
    point_cloud_max_z_range.from_value = -100.0;
    point_cloud_max_z_range.to_value = 100.0;
    point_cloud_max_z_desc.floating_point_range.push_back(point_cloud_max_z_range);
    point_cloud_max_z_ = declare_parameter("point_cloud_max_z", 100.0, point_cloud_max_z_desc);
  }
  {
    rcl_interfaces::msg::ParameterDescriptor occupancy_min_z_desc;
    occupancy_min_z_desc.description =
      "Minimum height of occupied cells to consider in the final map";
    rcl_interfaces::msg::FloatingPointRange occupancy_min_z_range;
    occupancy_min_z_range.from_value = -100.0;
    occupancy_min_z_range.to_value = 100.0;
    occupancy_min_z_desc.floating_point_range.push_back(occupancy_min_z_range);
    occupancy_min_z_ = declare_parameter("occupancy_min_z", -100.0, occupancy_min_z_desc);
  }
  {
    rcl_interfaces::msg::ParameterDescriptor occupancy_max_z_desc;
    occupancy_max_z_desc.description =
      "Maximum height of occupied cells to consider in the final map";
    rcl_interfaces::msg::FloatingPointRange occupancy_max_z_range;
    occupancy_max_z_range.from_value = -100.0;
    occupancy_max_z_range.to_value = 100.0;
    occupancy_max_z_desc.floating_point_range.push_back(occupancy_max_z_range);
    occupancy_max_z_ = declare_parameter("occupancy_max_z", 100.0, occupancy_max_z_desc);
  }
  min_x_size_ = declare_parameter("min_x_size", 0.0);
  min_y_size_ = declare_parameter("min_y_size", 0.0);

  {
    rcl_interfaces::msg::ParameterDescriptor filter_speckles_desc;
    filter_speckles_desc.description = "Filter speckle nodes (with no neighbors)";
    filter_speckles_ = declare_parameter("filter_speckles", false, filter_speckles_desc);
  }
  {
    rcl_interfaces::msg::ParameterDescriptor filter_ground_plane_desc;
    filter_ground_plane_desc.description = "Filter ground plane";
    filter_ground_plane_ =
      declare_parameter("filter_ground_plane", false, filter_ground_plane_desc);
  }
  {
    // distance of points from plane for RANSAC
    rcl_interfaces::msg::ParameterDescriptor ground_filter_distance_desc;
    ground_filter_distance_desc.description =
      "Distance threshold to consider a point as ground";
    rcl_interfaces::msg::FloatingPointRange ground_filter_distance_range;
    ground_filter_distance_range.from_value = 0.001;
    ground_filter_distance_range.to_value = 1.0;
    ground_filter_distance_desc.floating_point_range.push_back(ground_filter_distance_range);
    ground_filter_distance_ =
      declare_parameter("ground_filter.distance", 0.04, ground_filter_distance_desc);
  }
  {
    // angular derivation of found plane:
    rcl_interfaces::msg::ParameterDescriptor ground_filter_angle_desc;
    ground_filter_angle_desc.description =
      "Angular threshold of the detected plane from the horizontal plane to be detected as ground";
    rcl_interfaces::msg::FloatingPointRange ground_filter_angle_range;
    ground_filter_angle_range.from_value = 0.001;
    ground_filter_angle_range.to_value = 15.0;
    ground_filter_angle_desc.floating_point_range.push_back(ground_filter_angle_range);
    ground_filter_angle_ = declare_parameter("ground_filter.angle", 0.15);
  }
  {
    // distance of found plane from z=0 to be detected as ground (e.g. to exclude tables)
    rcl_interfaces::msg::ParameterDescriptor ground_filter_plane_distance_desc;
    ground_filter_plane_distance_desc.description =
      "Distance threshold from z=0 for a plane to be detected as ground";
    rcl_interfaces::msg::FloatingPointRange ground_filter_plane_distance_range;
    ground_filter_plane_distance_range.from_value = 0.001;
    ground_filter_plane_distance_range.to_value = 1.0;
    ground_filter_plane_distance_desc.floating_point_range.push_back(
      ground_filter_plane_distance_range
    );
    ground_filter_plane_distance_ =
      declare_parameter("ground_filter.plane_distance", 0.07, ground_filter_plane_distance_desc);
  }
  {
    rcl_interfaces::msg::ParameterDescriptor max_range_desc;
    max_range_desc.description = "Sensor maximum range";
    rcl_interfaces::msg::FloatingPointRange max_range_range;
    max_range_range.from_value = -1.0;
    max_range_range.to_value = 100.0;
    max_range_desc.floating_point_range.push_back(max_range_range);
    max_range_ = declare_parameter("sensor_model.max_range", -1.0, max_range_desc);
  }

  res_ = declare_parameter("resolution", 0.025); // le 0.025 est la val par defaut si rien mis dans le launch

  rcl_interfaces::msg::ParameterDescriptor prob_hit_desc;
  prob_hit_desc.description =
    "Probabilities for hits in the sensor model when dynamically building a map";
  rcl_interfaces::msg::FloatingPointRange prob_hit_range;
  prob_hit_range.from_value = 0.5;
  prob_hit_range.to_value = 1.0;
  prob_hit_desc.floating_point_range.push_back(prob_hit_range);
  const double prob_hit = declare_parameter("sensor_model.hit", 0.7, prob_hit_desc);

  rcl_interfaces::msg::ParameterDescriptor prob_miss_desc;
  prob_miss_desc.description =
    "Probabilities for misses in the sensor model when dynamically building a map";
  rcl_interfaces::msg::FloatingPointRange prob_miss_range;
  prob_miss_range.from_value = 0.0;
  prob_miss_range.to_value = 0.5;
  prob_miss_desc.floating_point_range.push_back(prob_miss_range);
  const double prob_miss = declare_parameter("sensor_model.miss", 0.4, prob_miss_desc);

  rcl_interfaces::msg::ParameterDescriptor prob_min_desc;
  prob_min_desc.description =
    "Minimum probability for clamping when dynamically building a map";
  rcl_interfaces::msg::FloatingPointRange prob_min_range;
  prob_min_range.from_value = 0.0;
  prob_min_range.to_value = 1.0;
  prob_min_desc.floating_point_range.push_back(prob_min_range);
  const double thres_min = declare_parameter("sensor_model.min", 0.12, prob_min_desc);

  rcl_interfaces::msg::ParameterDescriptor prob_max_desc;
  prob_max_desc.description =
    "Maximum probability for clamping when dynamically building a map";
  rcl_interfaces::msg::FloatingPointRange prob_max_range;
  prob_max_range.from_value = 0.0;
  prob_max_range.to_value = 1.0;
  prob_max_desc.floating_point_range.push_back(prob_max_range);
  const double thres_max = declare_parameter("sensor_model.max", 0.97, prob_max_desc);

  {
    rcl_interfaces::msg::ParameterDescriptor compress_map_desc;
    compress_map_desc.description = "Compresses the map losslessly";
    compress_map_ = declare_parameter("compress_map", true, compress_map_desc);
  }
  {
    rcl_interfaces::msg::ParameterDescriptor incremental_2D_projection_desc;
    incremental_2D_projection_desc.description = "Incremental 2D projection";
    incremental_2D_projection_ =
      declare_parameter("incremental_2D_projection", false, incremental_2D_projection_desc);
  }

  if (filter_ground_plane_ && (point_cloud_min_z_ > 0.0 || point_cloud_max_z_ < 0.0)) {
    RCLCPP_WARN_STREAM(
      get_logger(),
      "You enabled ground filtering but incoming pointclouds will be pre-filtered in [" <<
        point_cloud_min_z_ << ", " << point_cloud_max_z_ << "], excluding the ground level z=0. "
        "This will not work.");
  }

  if (use_height_map_ && use_colored_map_) {
    RCLCPP_WARN_STREAM(
      get_logger(),
      "You enabled both height map and RGB color registration. "
      "This is contradictory. Defaulting to height map.");
    use_colored_map_ = false;
  }

  if (use_colored_map_) {
#ifdef COLOR_OCTOMAP_SERVER
    RCLCPP_INFO_STREAM(get_logger(), "Using RGB color registration (if information available)");
#else
    RCLCPP_ERROR_STREAM(
      get_logger(),
      "Colored map requested in launch file - node not running/compiled to support colors, "
      "please define COLOR_OCTOMAP_SERVER and recompile or launch the octomap_color_server node");
#endif
  }

  // initialize octomap object & params
  octree_ = std::make_unique<OcTreeT>(res_);
  octree_->setProbHit(prob_hit);
  octree_->setProbMiss(prob_miss);
  octree_->setClampingThresMin(thres_min);
  octree_->setClampingThresMax(thres_max);
  tree_depth_ = octree_->getTreeDepth();
  max_tree_depth_ = tree_depth_;
  {
    rcl_interfaces::msg::ParameterDescriptor max_depth_desc;
    max_depth_desc.description =
      "Maximum depth when traversing the octree to send out markers."
      "16: full depth / max. resolution";
    rcl_interfaces::msg::IntegerRange max_depth_range;
    max_depth_range.from_value = 1;
    
    // modif de la porté du nuage de point de l'octomap (avant ; 16 )
    max_depth_range.to_value = 16; 
    
    
    max_depth_desc.integer_range.push_back(max_depth_range);
    declare_parameter("max_depth", static_cast<int64_t>(max_tree_depth_), max_depth_desc);
  }
  gridmap_.info.resolution = res_;
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
